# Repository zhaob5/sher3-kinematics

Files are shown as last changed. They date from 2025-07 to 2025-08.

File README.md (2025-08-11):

# SHER-3.0 Kinematics and Jacobian Analysis

This repository contains detailed derivations and explanations of the **forward kinematics**, **inverse kinematics**, **Jacobian**, and **Jacobian Inverse** analysis for the **SHER-3.0 surgical robot**. It includes analytical computation results in Python, validation through SolidWorks motion simulation, and detailed documentation for future insights and reference.

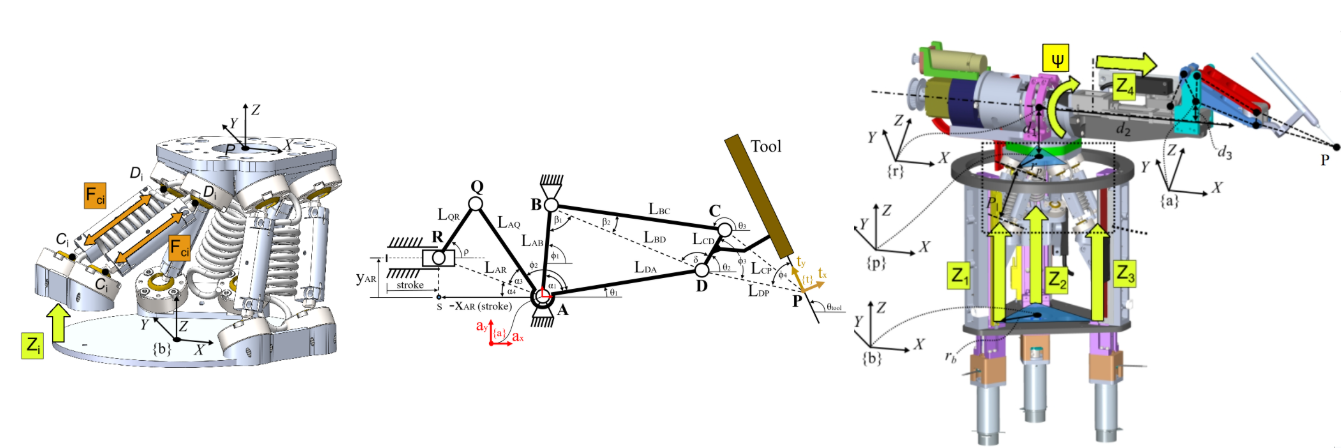
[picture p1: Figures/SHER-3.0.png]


## Recommended reading order:

1. **[Kinematics of a 3-PUU Delta-Style Parallel Robot](https://github.com/zhaob5/sher3-kinematics/blob/main/Kinematics%20of%20a%203-PUU%20Delta-Style%20Parallel%20Robot.pdf)** – foundational understanding of the delta platform.

2. **[Kinematics of the Roll-Tilt Mechanism in SHER-3.0](https://github.com/zhaob5/sher3-kinematics/blob/main/Kinematics%20of%20the%20Roll-Tilt%20Mechanism%20in%20SHER-3.0.pdf)** – breakdown of the rotating four-bar linkage structure.
   
3. **[(Optional) SOLIDWORKS Motion Study Tutorial: Setup and Kinematic Analysis for SHER-3.0](https://github.com/zhaob5/sher3-kinematics/blob/main/SOLIDWORKS%20Motion%20Study%20Tutorial%20Setup%20and%20Kinematic%20Analysis%20for%20SHER-3.0.pdf)** - a quick-start reference for running motion simulation in SOLIDWORKS.

4. **[Kinematics and Jacobian Analysis of SHER-3.0](https://github.com/zhaob5/sher3-kinematics/blob/main/Kinematics%20and%20Jacobian%20Analysis%20of%20SHER-3.0.pdf)** – full system modeling and differential kinematics.

5. **[Closed-Form Jacobian Inverse Derivation for SHER-3.0](https://github.com/zhaob5/sher3-kinematics/blob/main/Closed-Form%20Jacobian%20Inverse%20Derivation%20for%20SHER-3.0.pdf)** - derivation of the Jacobian Inverse with physical intuition.

## License

Copyright © 2025 JHU LCSR. Developed by Botao Zhao for [AMIRo Research Lab](https://amiro.lcsr.jhu.edu/).

See the [LICENSE](./LICENSE) file for details.

## Disclaimer

The derivation and analysis presented in this repository are based on analytical methods applied to a custom-designed robotic system. Readers are strongly encouraged to focus on the **methodology and reasoning** behind the derivations rather than relying solely on the final equations.

**Please independently verify all results before applying them to any critical or safety-sensitive applications.** This work is provided “as is” without warranty of any kind.

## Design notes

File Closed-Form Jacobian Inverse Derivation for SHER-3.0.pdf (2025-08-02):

## Closed-Form Jacobian Inverse Derivation for SHER-3.0

Botao Zhao

August 2, 2025

## Contents

1 Introduction | 2
2 SHER-3.0 at a Glance - and Why It’s Different | 2
3 Spatial Jacobian Inverse | 3
4 Body Jacobian Inverse | 8
5 Jacobian Inverse Validation | 8
6 Disclaimer | 9
7 Appendix: Python Scripts | 10

## 1 Introduction

In my previous work, Kinematics and Jacobian Analysis of SHER-3.0, I demonstrated that the robot’s Jacobian pseudo-inverse can be expressed as J

† = (J
T J)

−1J
T
, which is a common numerical method for computing the inverse. However, while numerical approaches are convenient, having an analytical (closed-form) Jacobian inverse is essential for achieving fast, stable, and insightful control — especially in real-time robotics applications.
For example, a robotic arm running at 500Hz. A numerical Jacobian inverse might take 1.8ms per control cycle - uncomfortably close to the 2ms timing constraint - whereas a symbolic expression, optimized in code, usually could reduce that time to under 0.5ms. Beyond performance, analytical forms also expose singularities, reduce numerical drift, and support optimization routines that rely on clean derivatives. They’re not just elegant - they’re highly practical!
This document walks through the step-by-step derivation of the analytical pseudo-inverse of the Jacobian for SHER-3.0 (Eye Robot 3.0). If you haven’t read my earlier work - especially Kinematics and Jacobian Analysis of SHER-3.0 and related documents, I strongly encourage you to review them first, as this work builds directly on those foundational concepts. Those related documents are avalible at: https://github.com/zhaob5/sher3-kinematics

## 2 SHER-3.0 at a Glance - and Why It’s Different

As mentioned throughout previous work, SHER-3.0 is a hybrid delta-serial robot designed specifi-cally for eye surgery, as illustrated in Fig.(1). Its unique structure, a delta platform coupled with a rotating four-bar linkage, sets it apart from most conventional ophthalmic surgical robots and presents significant challenges to traditional kinematic modeling approaches. My previous work has focused on deriving its kinematics in detail, and I hope those efforts will provide useful insights, or practical guidance for your own work.

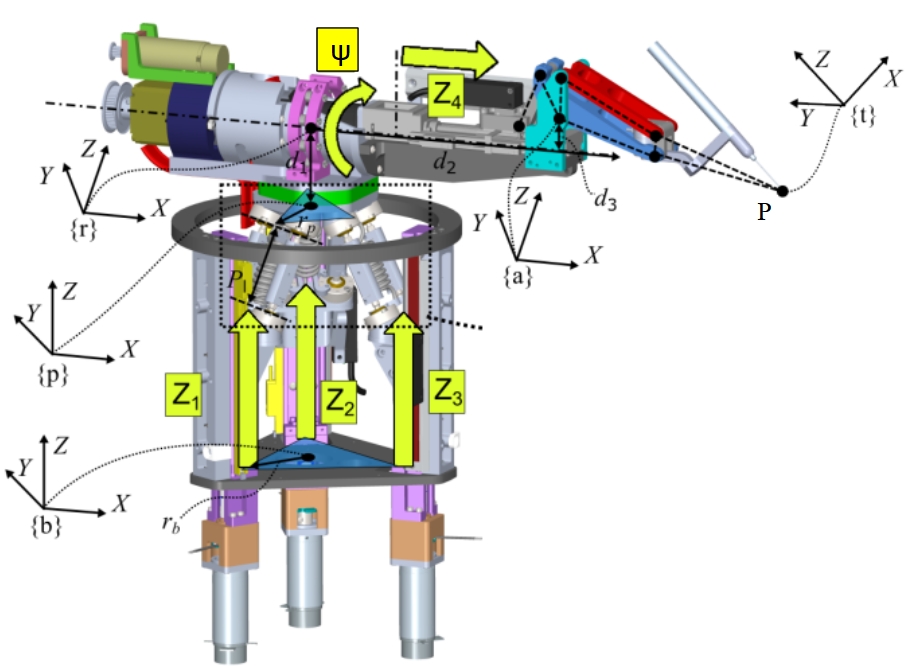
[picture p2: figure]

Figure 1: CAD models of the 5-DOF SHER-3.0 with assigned frames

## 3 Spatial Jacobian Inverse

Since we are not relying on numerical methods to compute the Jacobian inverse, it is important to first revisit its physical meaning. Suppose we want the tool tip to move with a desired spatial velocity Vtool = [ ˙x, y,˙ z,˙

˙θx,

˙θy,

˙θz]
T
. To achieve this motion, the robot must drive its joints at specific velocities ˙q = [ ˙q1, q˙2, q˙3, q˙4, q˙5]

T
. But how do we determine the required joint motions? This is where the Jacobian inverse comes in: it provides the mapping from task-space velocity to joint-space velocity. Our goal, therefore, is to derive this mapping from first principles, guided by physical intuition rather than black-box computation.

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
For simplicity, all Jacobians discussed in this section refer to the spatial Jacobian, and velocities are expressed in base frame.

Recall from Section-5.2 of Kinematics of a 3-PUU Delta-Style Parallel Robot, we derived the differential kinematics of the delta platform:

zli

q˙i = xlix˙ + yli

y˙ + zli

z˙ | (2)

where i = 1, 2, 3, and xli

, yli

, zli

are the x, y, z components of the vector along link li | . Here, ˙qi
denotes the linear velocity of the i-th prismatic joint, and ˙x, y,˙ z˙ represent the translational velocity of the delta platform in the base frame.

From this, we can directly relate the desired platform velocity to the corresponding joint velocities as:

q˙i =

xli
zli

x˙ +

yli
zli
y˙ + ˙z | (3)

Now, focusing just on the delta platform - if we know the desired linear velocity of the platform, the corresponding joint velocities can be directly computed from it as:

q˙1
q˙2
q˙3

delta

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
- (4)

This relationship effectively defines the top-left block of the Jacobian inverse.

Now let’s do some visualization: Although the roll and tilt joints appear to provide only angular motion, the tool tip is not located along their axes of rotation (as illustrated in Fig.2). In fact, due to the four-bar linkage, the tilt motion is mechanically coupled with translation. As a result, both roll and tilt inevitably produce linear motion in the x, y, z directions.

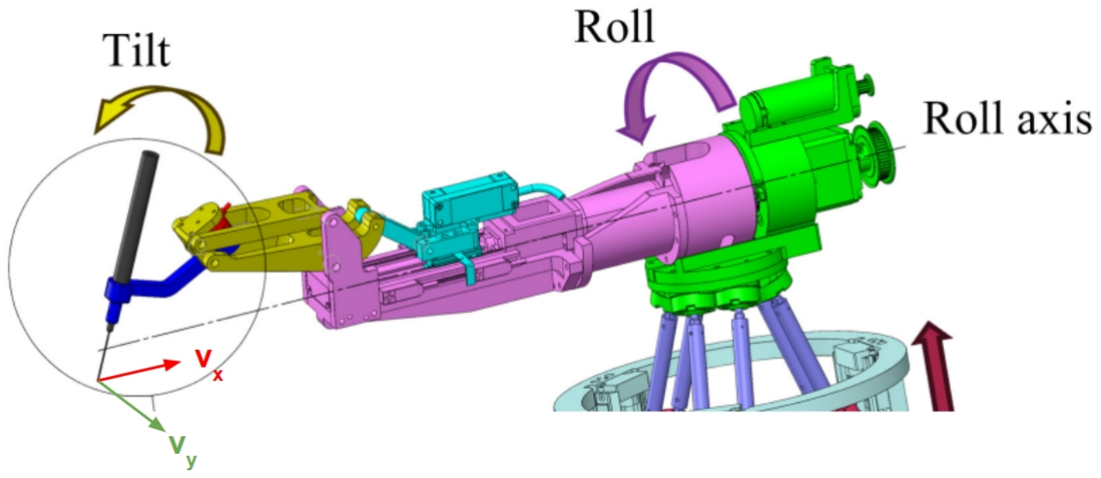
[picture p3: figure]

Figure 2: Roll-Tilt Mechanism and Induced Velocities vx and vy

Here comes the most challenging part to imagine: although angular velocities ˙θx,

˙θy,

˙θz will cause
nonzero ˙x, y,˙ z˙, these induced translations can be computed precisely. So, to isolate the translation purely caused by the roll-tilt mechanism, we can simply compensate (by subtracting) these induced linear velocities with the delta platform.

How do we know the linear velocity of tool tip in frame {p}? If we just look the roll-tilt mechanism, as we derived previously in Kinematics of the Roll-Tilt Mechanism in SHER-3.0, the translational velocity induced by the roll-tilt mechanism can be expressed as:

x˙
y˙
z˙

{p}

=

P˙
x{a}
− sin(ψ)P˙

y{a} − cos(ψ)ψ˙(Py{a} + d3) cos(ψ)P˙

y{a} − sin(ψ)ψ˙(Py{a} + d3)

- (5)

where

P˙

x{a} = − sin(θ1)LDA ˙θ1 − sin(θ2 − ϕ3)LDP ˙θ2

P˙

y{a} = cos(θ1)LDA ˙θ1 + cos(θ2 − ϕ3)LDP ˙θ2

(6)

and previously, we also derived the angular velocity of each link:

˙θ1 = −

LID

LDA

˙θ2

˙θ2 =

LDALJQ

LIDLAQLJR

s˙

(7)

Plug eq.(7) into eq.(6):

P˙
x{a} = (sin(θ1)LID − sin(θ2 − ϕ3)LDP )

˙θ2

P˙
y{a} = (− cos(θ1)LID + cos(θ2 − ϕ3)LDP )

˙θ2

(8)

Let:

C = sin(θ1)LID − sin(θ2 − ϕ3)LDP D = − cos(θ1)LID + cos(θ2 − ϕ3)LDP

(9)

Then

P˙

x{a} = C ˙θ2

P˙

y{a} = D ˙θ2

(10)

By plugging eq.(5) into eq.(4), we obtain the joint velocities required to compensate for the induced linear motion:

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
x{a}
− sin(ψ)P˙

y{a} − cos(ψ)ψ˙(Py{a} + d3) cos(ψ)P˙

y{a} − sin(ψ)ψ˙(Py{a} + d3)

(11)

Since we’re interested in understanding how the roll and tilt mechanisms contribute to this induced velocity, we aim to express eq.(11) explicitly in terms of the roll and tilt rates ψ˙ and ˙θ2. Substituting eq.(10) into eq.(11) yields:

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
C ˙θ2
− sin(ψ)D ˙θ2 − cos(ψ)(Py{a} + d3)ψ˙ cos(ψ)D ˙θ2 − sin(ψ)(Py{a} + d3)ψ˙

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
0 | C
− cos(ψ)(Py{a} + d3) − sin(ψ)D − sin(ψ)(Py{a} + d3) cos(ψ)D

ψ˙
˙θ2

=

−

yl1

zl1

cos(ψ)(Py{a} + d3) − sin(ψ)(Py{a} + d3)

xl1

zl1

C −

yl1

zl1

sin(ψ)D + cos(ψ)D
−

yl2

zl2

cos(ψ)(Py{a} + d3) − sin(ψ)(Py{a} + d3)

xl2

zl2

C −

yl2

zl2

sin(ψ)D + cos(ψ)D
−

yl3

zl3

cos(ψ)(Py{a} + d3) − sin(ψ)(Py{a} + d3)

xl3

zl3

C −

yl3

zl3

sin(ψ)D + cos(ψ)D

ψ˙
˙θ2

(12)

Now we have established the relationship between the joint velocities required to compensate for the induced linear motion and the angular velocities of the roll and tilt mechanisms.

However, we want to express these angular velocities in the base frame as [ ˙θx,

˙θy,

˙θz]
T
. To do
so, let’s recall the expression for the tool tip’s angular velocity previously derived in Kinematics of the Roll-Tilt Mechanism in SHER-3.0 :

˙θx
˙θy
˙θz

{p}

=

ψ˙
− cos(ψ)

˙θ2
− sin(ψ)

˙θ2

- (13)

Since there’s no rotational transformation between base frame {b} and delta platform frame {p}, it’s easy to figure out [ ˙θx,

˙θy,

˙θz]
T

{p} = [ ˙θx,

˙θy,

˙θz]
T
{b}

From eq.(13), it’s clear that although ˙θy and ˙θz appear to be independent, they are actually coupled through ψ and ˙θ2. In other words, specifying ˙θy determines a unique corresponding ˙θz and vice versa.
Since ψ˙ represents the rotational velocity about the base frame’s x axis, and we already have the relationship between ˙θy and ˙θ2 from eq.(13), we can substitute ψ˙ = ˙θx and ˙θ2 = −
1
cos(ψ)

˙θy into

eq.(12) to obtain:

q˙1
q˙2
q˙3
- =

−

yl1

zl1

cos(ψ)(Py{a} + d3) − sin(ψ)(Py{a} + d3)

xl1

zl1

C −

yl1

zl1

sin(ψ)D + cos(ψ)D
−

yl2

zl2

cos(ψ)(Py{a} + d3) − sin(ψ)(Py{a} + d3)

xl2

zl2

C −

yl2

zl2

sin(ψ)D + cos(ψ)D
−

yl3

zl3

cos(ψ)(Py{a} + d3) − sin(ψ)(Py{a} + d3)

xl3

zl3

C −

yl3

zl3

sin(ψ)D + cos(ψ)D

"
˙θx
−

1
cos(ψ)

˙θy

=

−

yl1

zl1

cos(ψ)(Py{a} + d3) − sin(ψ)(Py{a} + d3) −

xl1

zl1

cos(ψ)

C +

yl1

zl1

tan(ψ)D − D
−

yl2

zl2

cos(ψ)(Py{a} + d3) − sin(ψ)(Py{a} + d3) −

xl2

zl2

cos(ψ)

C +

yl2

zl2

tan(ψ)D − D
−

yl3

zl3

cos(ψ)(Py{a} + d3) − sin(ψ)(Py{a} + d3) −

xl3

zl3

cos(ψ)

C +

yl3

zl3

tan(ψ)D − D

˙θx
˙θy

(14)

Let

Mr =

−

yl1

zl1

cos(ψ)(Py{a} + d3) − sin(ψ)(Py{a} + d3) −

xl1

zl1

cos(ψ)

C +

yl1

zl1

tan(ψ)D − D
−

yl2

zl2

cos(ψ)(Py{a} + d3) − sin(ψ)(Py{a} + d3) −

xl2

zl2

cos(ψ)

C +

yl2

zl2

tan(ψ)D − D
−

yl3

zl3

cos(ψ)(Py{a} + d3) − sin(ψ)(Py{a} + d3) −

xl3

zl3

cos(ψ)

C +

yl3

zl3

tan(ψ)D − D

(15)

Then

q˙1
q˙2
q˙3

induced

= Mr

˙θx
˙θy

{b}

(16)

In this case, it’s clear that ˙θz has no effect on ˙q1, q˙2, q˙3. However, to maintain consistency with the full Jacobian inverse expression introduced later, we’ll add ˙θz to the right-hand side of eq.(16) to make it consistancy with later Jacobian Inverse expression:

q˙1
q˙2
q˙3

induced

= [Mr 0]

˙θx
˙θy
˙θz

{b}

(17)

Now, let’s combine eq.(4) and eq.(17). Note that the joint velocities from eq.(17) represent the linear velocity induced by roll and tilt, which is exactly the term that needs to be subtracted in our final Jacobian inverse formulation.

Thus:

q˙1
q˙2
q˙3
- =

q˙1
q˙2
q˙3

delta

−

q˙1
q˙2
q˙3

induced

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
- − [Mr 0]

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
1 −Mr[1,1] | −Mr[1,2] | 0

xl2

zl2

yl2

zl2

1 −Mr[2,1] | −Mr[2,2] | 0

xl3

zl3

yl3

zl3

1 −Mr[3,1] | −Mr[3,2] | 0

x˙
y˙
z˙
˙θx
˙θy
˙θz

{b}

(18)

From eq.(7), since ˙s = ˙q5 and ˙θ2 = −
1
cos(ψ)

˙θy, we can get the relationship between ˙q5 and ˙θy:

˙θ2 =

LDALJQ

LIDLAQLJR

s˙

−

1
cos(ψ)

˙θy =

LDALJQ

LIDLAQLJR

q˙5

(19)

Recall ψ is just q4. Rearrange eq.(19), and we will get:

q˙5 = −

LIDLAQLJR
cos(q4)LDALJQ
˙θy | (20)

Since ˙q4 = ψ˙ represents the rotational velocity about the base frame’s x axis,

q˙4 = ˙θx | (21)

Thus, we now have the final two components needed to construct the Jacobian inverse. By stacking eq.(20) and eq.(21) to eq.(18), we obtain:

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
1 −Mr[1,1] | −Mr[1,2] | 0

xl2

zl2

yl2

zl2

1 −Mr[2,1] | −Mr[2,2] | 0

xl3

zl3

yl3

zl3

1 −Mr[3,1] | −Mr[3,2] | 0
0 | 0 | 0 | 1 | 0 | 0
0 | 0 | 0 | 0 | −
| | | | LIDLAQLJR cos(q4)LDALJQ | 0

x˙
y˙
z˙
˙θx
˙θy
˙θz

(22)

Finally, the analytical expression of Spatial Jacobian Inverse is:

Js

−1 =

xl1

zl1

yl1

zl1

1 −Mr[1,1] | −Mr[1,2] | 0

xl2

zl2

yl2

zl2

1 −Mr[2,1] | −Mr[2,2] | 0

xl3

zl3

yl3

zl3

1 −Mr[3,1] | −Mr[3,2] | 0
0 | 0 | 0 | 1 | 0 | 0
0 | 0 | 0 | 0 | −
| | | | LIDLAQLJR cos(q4)LDALJQ | 0

(23)

## 4 Body Jacobian Inverse

In Kinematics and Jacobian Analysis of SHER-3.0, we defined a simplified adjoint-like mapping Ad†
(Tbt)

using only the rotation matrix:

Ad†
(Tbt) =
Rbt | 0
0 | Rbt
(24)

where Tbt is the homogeneous transformation from base frame {b} to tool frame {t}, and rotation matrix Rbt = Tbt[: 3, : 3].

Recall the relationship between Spatial and Body Jacobians:

Jb = Ad†
(Tbt)

−1
Js | (25)

Thus, we get the expression of the Body Jacobian Inverse:

Jb

−1 = Js

−1Ad†
(Tbt)

(26)

## 5 Jacobian Inverse Validation

In Kinematics and Jacobian Analysis of SHER-3.0, we previously verified the correctness of the forward Jacobian. Therefore, we will use that validated Jacobian as the ground truth Jtrue(q) in this section to verify the analytical Jacobian Inverse. The Python script used for verification is provided in the appendix.

To perform the verification, we first assign arbitrary joint positions q and joint velocities ˙qd. Using the verified Jacobian, we compute the corresponding tool tip velocities. These velocities are then fed into the Jacobian Inverse model. If the output joint velocities match the originally assigned (desired) values, the Jacobian Inverse is considered correct.

The verification workflow is as follows:

Vtool = Jtrue(q)˙qd

˙q = J(q)

−1Vtool

(27)

If ˙q = ˙qd, then the Jacobian Inverse is correct.

Consider the following random joint positions and velocities

q1
q2
q3
q4
q5

=

1 mm
2 mm
3 mm
31π
180 rad
11 mm

,

q˙1
q˙2
q˙3
q˙4
q˙5

=

7 mm/s
8 mm/s
9 mm/s
10π
180 rad/s
15 mm/s

The results are shown below:

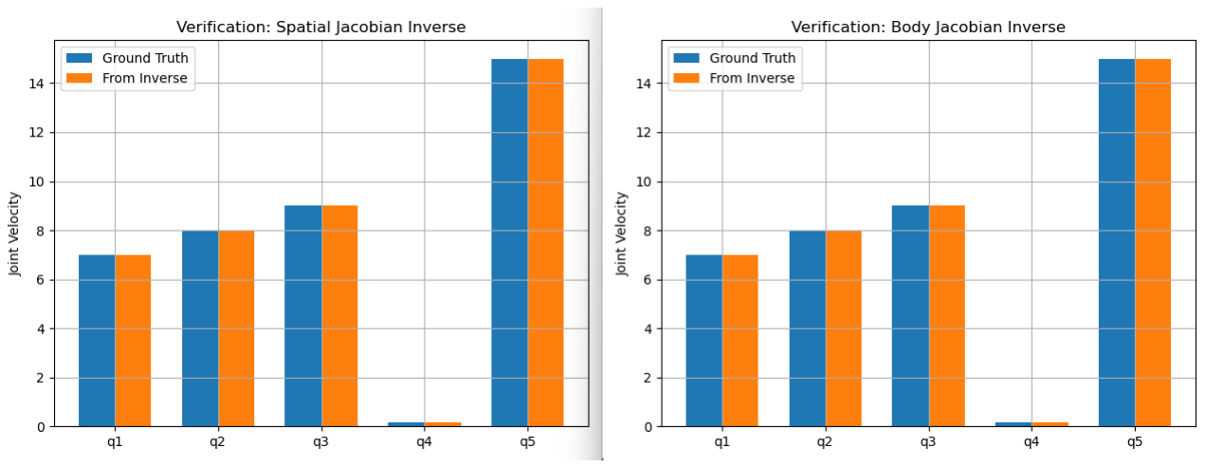
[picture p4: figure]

Figure 3: Joint Velocities Comparison

The joint velocities reconstructed using the analytical Jacobian inverse match the ground truth values across all joints. Thus, it confirms that the transformation from task-space velocities to joint-space velocities is accurate under the current kinematic model.

## 6 Disclaimer

The derivation process for the closed-form Jacobian inverse presented in this document is extremely tedious and prone to algebraic complexity. While every effort has been made to ensure the accuracy of the results, readers are strongly encouraged to focus on understanding the methodology and reasoning behind each step rather than relying solely on the final equations. If you plan to use these results in any critical applications, please independently verify all expressions and calculations for your specific use case. If you spot any errors, have suggestions, or would like to discuss the topic further, feel free to reach out to me at: bzhao17@alumni.jh.edu.

## 7 Appendix: Python Scripts

### 7.1 Jacobian Inverse Validation

1 | # -*- coding: utf-8 -*-
2 | """
3 | Created on Wed Jul 30 13:17:00 2025

4
5 | @author: Botao Zhao
6 | """

7
8 | import numpy as np
9 | from sympy import Matrix, zeros, pprint
10 | import matplotlib.pyplot as plt

11
12 | ################### Adjoint-like Mapping ###########################
13 | def adjoint_pseudo(T):
14 | R = T[:3, :3]
15 | return Matrix.vstack(
16 | Matrix.hstack(R, Matrix.zeros(3)),
17 | Matrix.hstack(Matrix.zeros(3), R)
18 | )

19
20 | ################### Joint Parameters: ##############################
21 | # Set desired Joint Positions Here:
22 | q1 = 1 | # Prismatic
23 | q2 = 2 | # Prismatic
24 | q3 = 3 | # Prismatic
25 | q4 = 31*np.pi/180 | # Revolute
26 | q5 = 11 | # Prismatic

27
28 | ################### Joint Velocities: ##############################
29 | # Set desired Joint Velocities Here:
30 | q1_dot = 7 | # mm/s
31 | q2_dot = 8 | # mm/s
32 | q3_dot = 9 | # mm/s
33 | q4_dot = 10*np.pi/180 | # rad/s
34 | q5_dot = 15 | # mm/s
35 | q_dot = Matrix([
36 | [q1_dot],
37 | [q2_dot],
38 | [q3_dot],
39 | [q4_dot],
40 | [q5_dot]
41 | ])

42
43 | ############################ Delta Platform: ###############################
44 | # Robot parameters
45 | rp = 34.4773 # mm platform radius
46 | rb = 60.6927 # mm base radius
47 | l = 68 | # mm rod length

48
49 | # Base joint angles
50 | theta1 = np.pi / 3
51 | theta2 = np.pi
52 | theta3 = 5 * np.pi / 3

53
54 | # Base joint positions (fixed)
55 | rb1 = np.array([np.cos(theta1)*rb, np.sin(theta1)*rb, 0])

rb2 = np.array([np.cos(theta2)*rb, np.sin(theta2)*rb, 0]) rb3 = np.array([np.cos(theta3)*rb, np.sin(theta3)*rb, 0])

# Platform offsets (relative to center)

rp1 = np.array([np.cos(theta1)*rp, np.sin(theta1)*rp, 0]) rp2 = np.array([np.cos(theta2)*rp, np.sin(theta2)*rp, 0]) rp3 = np.array([np.cos(theta3)*rp, np.sin(theta3)*rp, 0])

L1 = np.array([0,0,q1])
L2 = np.array([0,0,q2])
L3 = np.array([0,0,q3])

e1 = L1 + rb1 - rp1
e2 = L2 + rb2 - rp2
e3 = L3 + rb3 - rp3

h1 = ((e2[0]**2 + e2[1]**2 + e2[2]**2) - (e1[0]**2 + e1[1]**2 + e1[2]**2))/2 h2 = ((e3[0]**2 + e3[1]**2 + e3[2]**2) - (e1[0]**2 + e1[1]**2 + e1[2]**2))/2

x21 = (e2 - e1)[0]
y21 = (e2 - e1)[1]
z21 = (e2 - e1)[2]

x31 = (e3 - e1)[0]
y31 = (e3 - e1)[1]
z31 = (e3 - e1)[2]

k1 = (y31*z21/y21 - z31)/(x31 - y31*x21/y21) k2 = (h2 - y31*h1/y21)/(x31 - y31*x21/y21) k3 = (x31*z21/x21 - z31)/(y31 - x31*y21/x21) k4 = (h2 - x31*h1/x21)/(y31 - x31*y21/x21)

T1 = k1**2 + k3**2 + 1
T2 = k1*k2 + k3*k4 - e1[0]*k1 - e1[1]*k3 - e1[2]
T3 = k2**2 + k4**2 -2*e1[0]*k2 - 2*e1[1]*k4 - l**2 + e1[0]**2 + e1[1]**2 + e1[2]**2

z = (-T2 + np.sqrt(T2**2 - T1*T3))/T1
x = k1*z + k2
y = k3*z + k4

r = np.array([x, y, z])

l1 = -L1 - rb1 + r + rp1
l2 = -L2 - rb2 + r + rp2
l3 = -L3 - rb3 + r + rp3

########################## Roll-Tilt Mechanism: ###########################

s = q5 # slider linear actuator
s_dot = q5_dot # slider velocity
psi = q4 # roll angle

# Fixed Parameters

x_AR_max = 60.48
y_AR = -10
L_AQ = 32.5
L_QR = 42

L_AB = 28
L_BC = 78.5
L_CD = 15
L_DA = 73.5
phi1 = np.pi / 2
phi2 = np.pi * 138 / 180
L_DP = 94.49
phi3 = np.pi * 103.93 / 180
phi4 = np.pi * 31.06 / 180
L_T = 50
d1 = 56.01 # Distance between the center frame of the delta platform to point A d2 = 192.7
d3 = 25.5

# Fixed angles in radians

phi1 = np.pi / 2
phi2 = np.pi * 138 / 180
phi3 = np.pi * 103.93 / 180 phi4 = np.pi * 31.06 / 180

# Position Analysis

x_AR = x_AR_max - s
L_AR = np.sqrt(x_AR**2 + y_AR**2)
alpha3 = np.arccos((L_AR**2 + L_AQ**2 - L_QR**2) / (2 * L_AR * L_AQ)) alpha4 = np.pi - np.arctan2(y_AR, -x_AR)
alpha = alpha3 + alpha4

theta1 = np.pi - (phi2 + alpha3 + alpha4)
alpha_1 = phi1 - theta1
L_BD = np.sqrt(L_AB**2 + L_DA**2 - 2 * L_AB * L_DA * np.cos(alpha_1)) beta_1 = np.arccos((L_AB**2 + L_BD**2 - L_DA**2) / (2 * L_AB * L_BD))

delta = np.arccos((L_CD**2 + L_BD**2 - L_BC**2) / (2 * L_CD * L_BD)) theta2 = phi1 + beta_1 - delta

# Velocity Analysis

L_JR = np.tan(alpha)*x_AR - y_AR
L_JQ = np.sqrt((L_JR+y_AR)**2 + x_AR**2) - L_AQ

rho_dot = s_dot / L_JR
theta1_dot = -L_JQ / L_AQ * rho_dot

beta_2 = np.arccos((L_BC**2 + L_BD**2 - L_CD**2) / (2 * L_BC * L_BD)) L_IA = L_AB * np.sin(beta_1 + beta_2) / np.sin(alpha_1 + beta_1 + beta_2) L_ID = L_IA - L_DA

theta2_dot = -L_DA / L_ID * theta1_dot

# Position in {a} frame:

px_a = np.cos(theta1)*L_DA + np.cos(theta2 - phi3)*L_DP py_a = np.sin(theta1)*L_DA + np.sin(theta2 - phi3)*L_DP

# Position in {p} frame:

px_p = px_a + d2
py_p = -np.sin(psi)*py_a - np.sin(psi)*d3 pz_p = np.cos(psi)*py_a + np.cos(psi)*d3 + d1

# Position in {b} frame:

px_b = px_a + d2 + x py_b = -np.sin(psi)*py_a - np.sin(psi)*d3 + y pz_b = np.cos(psi)*py_a + np.cos(psi)*d3 + d1 + z

# print([px_p, py_p, pz_p])

########## Homogeneous Transformation from Base frame to Tool frame ########### # Tbt

theta = np.pi/2 - phi4 - phi3 + theta2
Tbt = Matrix([
[np.cos(theta), -np.sin(theta), 0, px_a+d2+x],
[-np.sin(theta)*np.sin(psi), -np.cos(theta)*np.sin(psi), -np.cos(psi), -np.sin(psi)*py_a-np.sin(psi)*d3+y], [np.sin(theta)*np.cos(psi), np.cos(theta)*np.cos(psi), -np.sin(psi), np.cos(psi)*py_a+np.cos(psi)*d3+d1+z], [0, 0, 0, 1]
]) # 4x4 transformation from base to tool
Rbt = Tbt[:3, :3]

# Compute Ad_Tbt¹

Ttb = Tbt.inv()
Ad_Ttb = adjoint_pseudo(Ttb)

################### Spatial Jacobian Inverse (Analytical) #################

JacobianInvTip = zeros(5,6)

C = np.sin(theta1)*L_ID - np.sin(theta2-phi3)*L_DP D = -np.cos(theta1)*L_ID + np.cos(theta2-phi3)*L_DP

M_r = zeros(3,2)
M_r[0,0] = -l1[1]/l1[2] * np.cos(psi) * (py_a + d3) - np.sin(psi)*(py_a + d3) M_r[0,1] = -l1[0]/(l1[2]*np.cos(psi)) * C + l1[1]/l1[2]*np.tan(psi)*D - D

M_r[1,0] = -l2[1]/l2[2] * np.cos(psi) * (py_a + d3) - np.sin(psi)*(py_a + d3) M_r[1,1] = -l2[0]/(l2[2]*np.cos(psi)) * C + l2[1]/l2[2]*np.tan(psi)*D - D

M_r[2,0] = -l3[1]/l3[2] * np.cos(psi) * (py_a + d3) - np.sin(psi)*(py_a + d3) M_r[2,1] = -l3[0]/(l3[2]*np.cos(psi)) * C + l3[1]/l3[2]*np.tan(psi)*D - D

JacobianInvTip[0,0] = l1[0]/l1[2]
JacobianInvTip[1,0] = l2[0]/l2[2]
JacobianInvTip[2,0] = l3[0]/l3[2]

JacobianInvTip[0,1] = l1[1]/l1[2] JacobianInvTip[1,1] = l2[1]/l2[2] JacobianInvTip[2,1] = l3[1]/l3[2]

JacobianInvTip[0,2] = 1
JacobianInvTip[1,2] = 1
JacobianInvTip[2,2] = 1

JacobianInvTip[0:3, 3:5] = -M_r

JacobianInvTip[3,3] = 1

JacobianInvTip[4,4] = -L_ID*L_AQ*L_JR/(np.cos(q4)*L_DA*L_JQ)

JacobianInvTip[4,5] = 0 #

233
234 Js_inv = JacobianInvTip # 5x6 Spatial Jacobian Inverse

235

236

237
238 | ################ Body Jacobian Inverse | (Analytical) ################
239 | Ad_Tbt = adjoint_pseudo(Ttb).T

240
241 | # Compute body Jacobian
242 | Jb_inv = Js_inv * Ad_Tbt # 5x6 Body Jacobian Inverse

243

244
245 | ################ Spatial Jacobian ##############
246 | J_l = zeros(3,3)

247
248 | J_l[0,0] = l1[0]
249 | J_l[0,1] = l1[1]
250 | J_l[0,2] = l1[2]
251 | J_l[1,0] = l2[0]
252 | J_l[1,1] = l2[1]
253 | J_l[1,2] = l2[2]
254 | J_l[2,0] = l3[0]
255 | J_l[2,1] = l3[1]
256 | J_l[2,2] = l3[2]

257
258 J_z = zeros(3,3)

259
260 | J_z[0,0] = l1[2]
261 | J_z[1,1] = l2[2]
262 | J_z[2,2] = l3[2]

263
264 J_d = J_l.inv() * J_z

265
266 | A = np.sin(theta1)*L_DA*L_JQ/(L_AQ*L_JR) - np.sin(theta2-phi3)*L_DP*L_DA*L_JQ/(L_ID*L_AQ*L_JR)
267 | B = -np.cos(theta1)*L_DA*L_JQ/(L_AQ*L_JR) + np.cos(theta2-phi3)*L_DP*L_DA*L_JQ/(L_ID*L_AQ*L_JR)

268
269 JacobianTip = zeros(6,5)

270
271 JacobianTip[:3, :3] = J_d

272
273 | JacobianTip[1,3] = -np.cos(q4)*(py_a + d3)
274 | JacobianTip[2,3] = -np.sin(q4)*(py_a + d3)
275 | JacobianTip[3,3] = 1

276
277 | JacobianTip[0,4] = A
278 | JacobianTip[1,4] = -np.sin(q4)*B
279 | JacobianTip[2,4] = np.cos(q4)*B
280 | JacobianTip[4,4] = -np.cos(q4)*L_DA*L_JQ/(L_ID*L_AQ*L_JR)
281 | JacobianTip[5,4] = -np.sin(q4)*L_DA*L_JQ/(L_ID*L_AQ*L_JR)

282
283 | Js = JacobianTip | # 6x5 spatial Jacobian

284

285

286
287 ################# Body Jacobian ###################

288
289 # Tbt is known

290
291 # Compute body Jacobian

Jb = Ad_Ttb * Js

################# Tool Tip Velocity ################## V_tool_t = Jb*q_dot

V_tool_b = Js*q_dot

# print("\nIn base frame:\n")

# print("x_dot_b = ", V_tool_b[0], "mm/s")

# print("y_dot_b = ", V_tool_b[1], "mm/s")

# print("z_dot_b = ", V_tool_b[2], "mm/s")

# print("theta_x_dot_b = ", V_tool_b[3]*180/np.pi, "deg/s") # print("theta_y_dot_b = ", V_tool_b[4]*180/np.pi, "deg/s") # print("theta_z_dot_b = ", V_tool_b[5]*180/np.pi, "deg/s\n")

# print("\nIn tool frame:\n")

# print("x_dot_t = ", V_tool_t[0], "mm/s")

# print("y_dot_t = ", V_tool_t[1], "mm/s")

# print("z_dot_t = ", V_tool_t[2], "mm/s")

# print("theta_x_dot_t = ", V_tool_t[3]*180/np.pi, "deg/s") # print("theta_y_dot_t = ", V_tool_t[4]*180/np.pi, "deg/s") # print("theta_z_dot_t = ", V_tool_t[5]*180/np.pi, "deg/s\n")

################ Jacobian Inverse Verification ##################

q_dot_verify_s = Js_inv * V_tool_b
q_dot_verify_b = Jb_inv * V_tool_t

# print("Joint Velocity from Jacobian Pseudo-Inverse:")

# print("q_dot_s =")

# pprint(q_dot_verify_s) # The results should match your q_dot values # print("q_dot_b =")

# pprint(q_dot_verify_b) # The results should match your q_dot values

################### Visualization ##############################

def visualize_joint_velocity_comparison(original, computed, title): original_np = np.array(original).astype(np.float64).flatten() computed_np = np.array(computed).astype(np.float64).flatten()

joint_labels = [f'q{i+1}' for i in range(len(original_np))] x = np.arange(len(joint_labels))
width = 0.35

fig, ax = plt.subplots()
ax.bar(x - width/2, original_np, width, label='Ground Truth') ax.bar(x + width/2, computed_np, width, label='From Inverse')

ax.set_ylabel('Joint Velocity')
ax.set_title(title)
ax.set_xticks(x)
ax.set_xticklabels(joint_labels) ax.legend()
ax.grid(True)

plt.tight_layout()

351 | plt.show()

352
353 | # Visualize results
354 | visualize_joint_velocity_comparison(q_dot, q_dot_verify_s, "Verification: Spatial Jacobian Inverse")
355 | visualize_joint_velocity_comparison(q_dot, q_dot_verify_b, "Verification: Body Jacobian Inverse")

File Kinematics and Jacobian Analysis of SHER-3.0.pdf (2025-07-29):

## Kinematics and Jacobian Analysis of SHER-3.0

Botao Zhao

July 29, 2025

## Contents

1 Introduction | 2
2 System Overview | 2
3 Jacobian Matrix of SHER-3.0 | 3
4 Jacobian Pseudo-inverse of SHER-3.0 | 7
5 Validation with SolidWorks Motion Analysis | 8
6 Disclaimer | 11
7 Appendix: Python Scripts | 12

## 1 Introduction

The purpose of this document is to show detailed derivation of Jacobian matrix and Jacobian pseudo-inverse of SHER-3.0 (Eye Robot 3.0). Two separate documents covering the kinematic derivation of the delta platform and the roll-tilt mechanism are available at https://github.com/zhaob5/delta_kinematics (https://github.com/zhaob5/delta_kinematics) and https://github.com/zhaob5/roll_tilt_mechanism. If you haven’t read them yet, I strongly encourage you to review those two documents, as a lot expla-nations here build upon concepts introduced there. Some related papers and scripts can be found on this github page: https://github.com/zhaob5/Kinematics-and-Jacobian-Analysis-of-SHER-3. 0 (https://github.com/zhaob5/Kinematics-and-Jacobian-Analysis-of-SHER-3.0)

## 2 System Overview

The base of SHER-3.0 is a delta mechanism, which has been described in detail in my previous work. Mounted on top of the delta stage is an arm with roll and tilt functionality. The tilt mechanism was designed with a four-bar linkage configuration, as illustrated in Fig.(1) and Fig.(2).


Figure 1: CAD models of the 5-DOF SHER-3.0 with assigned frames

## 3 Jacobian Matrix of SHER-3.0

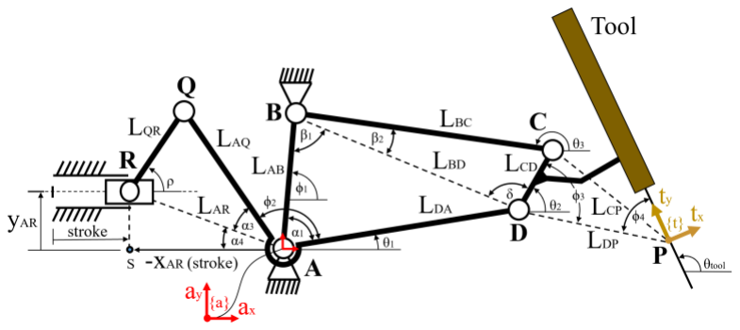
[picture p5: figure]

Figure 2: Side view of the tilt mechanism

### 3.1 Homogeneous Transformation from Base Frame to Tool Frame

Note that the coordinate frames {a} and {t} shown in Fig.1 and Fig.2 have different orientations. In this document, I will use the frame definition shown in Fig.2 to maintain consistency with my previous documentation. If a different frame is chosen, the resulting expressions will differ accordingly.

Since the delta platform provides only translational motion along x, y, z, its homogeneous transformation matrix has the following form:

Tbp =

I r
0 1
(1)

where r = [rx, ry, rz]

T
is the position vector from base frame {b} to platform frame {p}.

In Kinematics of the Roll-Tilt Mechanism in SHER-3.0, we derived:

Tat =

cos(θ) − sin(θ) 0 Px
sin(θ) | cos(θ) | 0 Py
0 | 0 | 1 | 0
0 | 0 | 0 | 1

(2)

Tpa =

1 | 0 | 0 | d2
0 − sin(ψ) − cos(ψ) | − sin(ψ)d3
0 | cos(ψ) | − sin(ψ) cos(ψ)d3 + d1
0 | 0 | 0 | 1

(3)

Thus, the transformation from base frame to tool frame is:

Tbt = TbpTpaTat

=

cos(θ) | − sin(θ) | 0 | Px + d2 + rx
− sin(θ) sin(ψ) − cos(θ) sin(ψ) − cos(ψ) | − sin(ψ)Py − sin(ψ)d3 + ry
sin(θ) cos(ψ) | cos(θ) cos(ψ) | − sin(ψ) cos(ψ)Py + cos(ψ)d3 + d1 + rz
0 | 0 | 0 | 1

(4)

### 3.2 Spatial Jacobian

A brief recap of the Spatial Jacobian: it maps joint velocities to the tool tip velocity, vtool = [ ˙x, y,˙ z,˙

˙θx,

˙θy,

˙θz]
T
, expressed in the base frame {b}.

x˙
y˙
z˙
˙θx
˙θy
˙θz

{b}

= Js

q˙1
q˙2
q˙3
q˙4
q˙5

(5)

Since q1, q2, q3 only generate translational motion, the upper-left 3×3 block of the Spatial Jacobian Js corresponds to the Jacobian of the delta platform, Jd, which was derived in Kinematics of a 3-PUU Delta-Style Parallel Robot:

Jd =

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
| 0 | 0
0 | zl2 | 0
0 | 0 | zl3
- (6)

Similarly, the lower-right 3×2 block of the Spatial Jacobian is only related to q4 and q5 since only q4 and q5 can provide rotational velocity.

Now things become a bit more complex. As previously mentioned, due to the nature of the four-bar linkage, q5 induces both rotational and translational motion, and q4 contributes to linear velocity as well, since the tool tip is offset from its axis of rotation.

Let’s break this down and construct the Spatial Jacobian one by one.

Recall in Kinematics of the Roll-Tilt Mechanism in SHER-3.0, we derived the tool tip velocity in the delta platform frame {p} as:

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
x{a}
− sin(ψ)P˙

y{a} − cos(ψ)ψ˙(Py{a} + d3) cos(ψ)P˙

y{a} − sin(ψ)ψ˙(Py{a} + d3) ψ˙
− cos(ψ)

˙θ2
− sin(ψ)

˙θ2

(7)

where
P˙

x{a} = − sin(θ1)LDA ˙θ1 − sin(θ2 − ϕ3)LDP ˙θ2

P˙

y{a} = cos(θ1)LDA ˙θ1 + cos(θ2 − ϕ3)LDP ˙θ2

θ1 = 180◦ − (ϕ2 + α3 + α4)

θ2 = β1 + ϕ1 − δ

(8)

and previously, we also derived the angular velocity of each link:

˙θ1 = −

LID

LDA

˙θ2

˙θ2 =

LDALJQ

LIDLAQLJR

s˙

(9)

Plug eq.(9) into eq.(8):

P˙
x{a} =
sin(θ1)

LDALJQ

LAQLJR

− sin(θ2 − ϕ3)

LDPLDALJQ

LIDLAQLJR
s˙

P˙
y{a} =
− cos(θ1)

LDALJQ

LAQLJR

+ cos(θ2 − ϕ3)

LDPLDALJQ

LIDLAQLJR
s˙

(10)

Let:

A =

sin(θ1)

LDALJQ

LAQLJR

− sin(θ2 − ϕ3)

LDPLDALJQ

LIDLAQLJR

B =

− cos(θ1)

LDALJQ

LAQLJR

+ cos(θ2 − ϕ3)

LDPLDALJQ

LIDLAQLJR | (11)

Since ψ˙ = ˙q4 and ˙s = ˙q5, we can rewrite eq.(7) as:

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
0 | A
− cos(ψ)(Py{a} + d3) | − sin(ψ)B
− sin(ψ)(Py{a} + d3) | cos(ψ)B
1 | 0
0 | − cos(ψ) LDALJQ LIDLAQLJR
0 | − sin(ψ) LDALJQ LIDLAQLJR

q˙4
q˙5
(12)

Because there is no rotation between the base frame {b} and the delta platform frame {p}, the velocity of the tool tip expressed in {b} is simply the sum of the delta platform’s velocity (in {b}) and the tool tip’s velocity in fixed {p} frame.

With that, we now have all the components needed to construct the Spatial Jacobian:

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
Jd[1,1] | Jd[1,2] | Jd[1,3] | 0 | A
Jd[2,1] | Jd[2,2] | Jd[2,3] | − cos(ψ)(Py{a} + d3) | − sin(ψ)B
Jd[3,1] | Jd[3,2] | Jd[3,3] | − sin(ψ)(Py{a} + d3) | cos(ψ)B
0 | 0 | 0 | 1 | 0
0 | 0 | 0 | 0 | − cos(ψ) LDALJQ LIDLAQLJR
0 | 0 | 0 | 0 | − sin(ψ) LDALJQ LIDLAQLJR

q˙1
q˙2
q˙3
q˙4
q˙5

(13)

Since ψ = q4, the Spatial Jacobian is:

Js =

Jd[1,1] | Jd[1,2] | Jd[1,3] | 0 | A
Jd[2,1] | Jd[2,2] | Jd[2,3] | − cos(q4)(Py{a} + d3) | − sin(q4)B
Jd[3,1] | Jd[3,2] | Jd[3,3] | − sin(q4)(Py{a} + d3) | cos(q4)B
0 | 0 | 0 | 1 | 0
0 | 0 | 0 | 0 | − cos(q4) LDALJQ LIDLAQLJR
0 | 0 | 0 | 0 | − sin(q4) LDALJQ LIDLAQLJR

(14)

### 3.3 Body Jacobian

Similar to the Spatial Jacobian, the Body Jacobian also maps joint velocities to the tool tip velocity, but expressed in the tool frame {t}.

x˙
y˙
z˙
˙θx
˙θy
˙θz

{t}

= Jb

q˙1
q˙2
q˙3
q˙4
q˙5

(15)

In the traditional formulation of robot kinematics, twists (which combine angular and linear velocity) are often used in conjunction with exponential coordinates and homogeneous transformation matrices. When switching between spatial and body frames, the adjoint transformation is typically applied as:

Vbody = Ad(T
−1
bt )Vspatial | (16)

where Ad(T
−1
bt )

is the adjoint matrix of the inverse transformation from the base frame {b} to the tool frame {t}. This standard adjoint takes both rotation and translation into account:

Ad(T) =

R 0

[p]R R
(17)

Here, R is the rotation matrix from one frame to another, p is the position vector between origins, and [p] is the skew-symmetric matrix of p.

However, in our case, we are not using twist representation or exponential coordinates directly. Instead, we are dealing with raw velocity vectors: stacked linear and angular velocity components in the form [v; ω]. These do not contain the full twist structure and lack the translational offset context needed for the full adjoint to apply correctly.

As such, the traditional adjoint would incorrectly mix rotational and translational effects when applied to our representation. To transform raw velocity vectors between frames, only the rotation part should be applied to each component separately. For example, vt = Rtbvb and ωt = Rtbωb.

Thus, we define a simplified adjoint-like mapping Ad†
(Ttb)

using only the rotation matrix:

Ad†
(Ttb) =
Rtb | 0
0 | Rtb
(18)

where Rtb = Rbt

T = Tbt[: 3, : 3]

T
, and Tbt is already been derived in eq.(4).

Finally, we get the expression of the Body Jacobian:

Jb = Ad†
(Ttb)Js | (19)

## 4 Jacobian Pseudo-inverse of SHER-3.0

In robotic kinematics, the Jacobian matrix J ∈ R

6×n maps joint velocities ˙q ∈ R
n
to end-effector
velocity v ∈ R

6
, and Jacobian inverse does the opposite thing as:

v = J ˙q

˙q = J

−1v

(20)

This works well when the number of joints n = 6, making J square and (if full rank) invertible. However, in our case, we only have 5 joints, so the Jacobian is a 6×5 matrix. That means it’s not directly invertible and no exact solution may exist for a general 6D velocity command.

To resolve this, we use the Moore-Penrose pseudo-inverse of the Jacobian, denoted J

† =
(J

T J)

−1J
T
, to find a least-squares optimal solution for the joint velocities ˙q that best approxi-mates the desired end-effector velocity:
˙q = J
†v | (21)

This gives us the joint velocity vector that minimizes the squared error between the actual and desired end-effector motion. It essentially ”projects” the 6D desired velocity into the 5D space of achievable motions.

### 4.1 Spatial Jacobian Pseudo-inverse

Since the Moore-Penrose pseudo-inverse is a general-purpose mathematical tool that can be applied to any non-square Jacobian matrix, it works for both Spatial and Body Jacobians.

Thus,
Js

† = (Js
T Js)

−1Js
T
(22)

˙q = Js

†vs | (23)

### 4.2 Body Jacobian Pseudo-inverse

Similarly,
Jb

† = (Jb
T Jb)

−1Jb
T
(24)

˙q = Jb

†vb | (25)

## 5 Validation with SolidWorks Motion Analysis

To validate the kinematic calculations presented in this document, I used SolidWorks to build a simplified CAD model of the SHER-3.0 mechanism. The assembly was constructed without incorporating any built-in kinematic constraints or control logic—only individual parts and their mechanical relationships were defined.

A motion simulation was then performed with SolidWorks Motion Study. Since SolidWorks Motion Simulation does not provide instantaneous velocity outputs at a specific configuration, I set the total simulation time to 0.5 seconds and observed the velocity values at time t=0.

At the initial moment, the model has not yet moved significantly, so the velocity at t=0 effec-tively represents the instantaneous velocity of the system at the given joint configuration. This allows for a valid comparison between the simulation results and the analytical velocity computed using the Jacobian-based method described in this document.

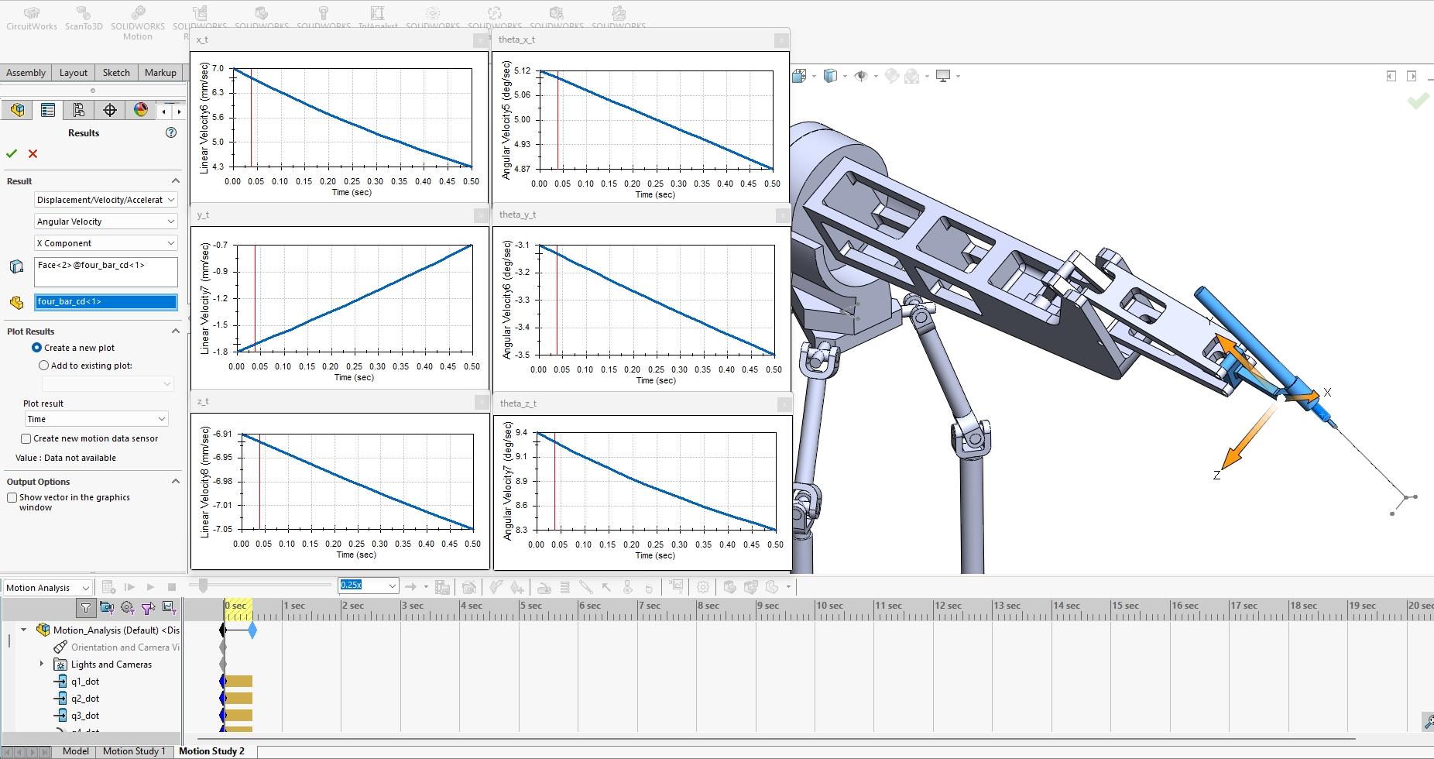
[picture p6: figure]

Figure 3: Motion Simulation Setup in SolidWorks

To test the model with arbitrary values, consider the following joint positions and velocities:

q1
q2
q3
q4
q5

=

1 mm
2 mm
3 mm
π
6

rad
10 mm

,

q˙1
q˙2
q˙3
q˙4
q˙5

=

4 mm/s
5 mm/s
6 mm/s
π
30 rad/s
10 mm/s

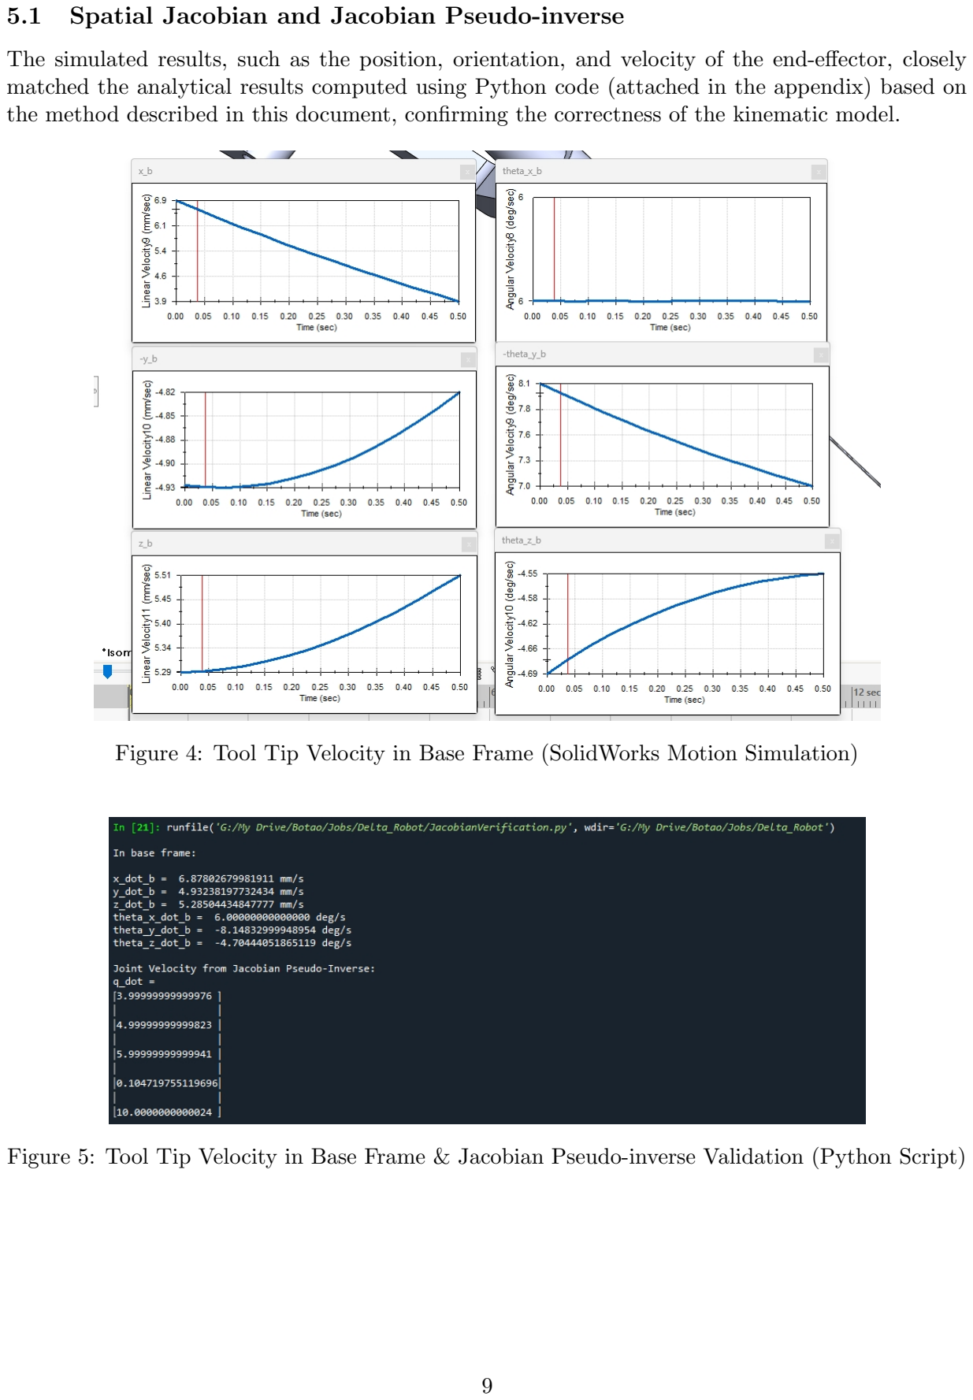
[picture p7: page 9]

### 5.1 Spatial Jacobian and Jacobian Pseudo-inverse

The simulated results, such as the position, orientation, and velocity of the end-effector, closely matched the analytical results computed using Python code (attached in the appendix) based on the method described in this document, confirming the correctness of the kinematic model.

Figure 4: Tool Tip Velocity in Base Frame (SolidWorks Motion Simulation)

Figure 5: Tool Tip Velocity in Base Frame & Jacobian Pseudo-inverse Validation (Python Script)

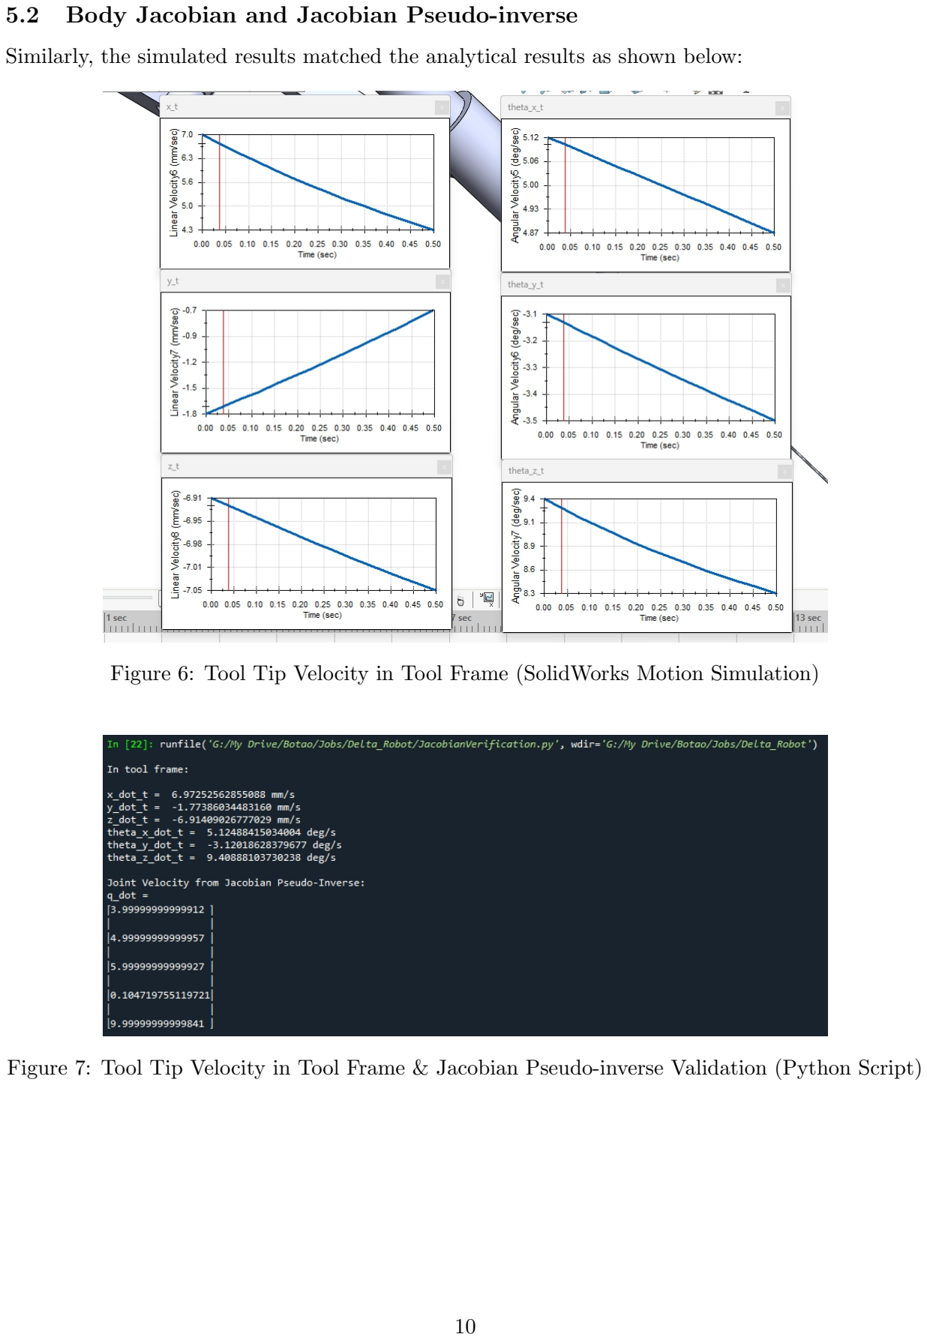
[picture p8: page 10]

### 5.2 Body Jacobian and Jacobian Pseudo-inverse

Similarly, the simulated results matched the analytical results as shown below:

Figure 6: Tool Tip Velocity in Tool Frame (SolidWorks Motion Simulation)

Figure 7: Tool Tip Velocity in Tool Frame & Jacobian Pseudo-inverse Validation (Python Script)

## 6 Disclaimer

The simulations and Jacobian-based calculations presented in this document are based on my personal understanding of the kinematic structure of SHER-3.0. Due to the complexity of the Jacobian—especially in systems involving multiple frames and mixed translational and rotational joints—there may be discrepancies between analytical results and simulation outputs. While the SolidWorks motion simulation validates the general correctness of the method, it is not guaranteed to match perfectly due to potential simplifications, numerical errors, or modeling assumptions. I encourage readers to focus on the methodology and reasoning behind the derivations rather than relying solely on the final equations. Please independently verify the results before applying them to any critical applications. If you spot any errors, have suggestions, or would like to discuss the topic further, feel free to reach out to me at: bzhao17@alumni.jh.edu.

## 7 Appendix: Python Scripts

### 7.1 Jacobian & Jacobian Pseudo-inverse Validation

1 | # -*- coding: utf-8 -*-
2 | """
3 | Created on Sun Jul 27 15:24:01 2025

4
5 | @author: Botao
6 | """

7
8 | import numpy as np
9 | from sympy import Matrix, zeros, pprint

10
11 | ################### Joint Parameters: ##############################
12 | q1 = 1 | # Prismatic
13 | q2 = 2 | # Prismatic
14 | q3 = 3 | # Prismatic
15 | q4 = 30*np.pi/180 | # Revolute
16 | q5 = 10 | # Prismatic

17
18 | ################### Joint Velocities: ##############################
19 | q1_dot = 4 | # mm/s
20 | q2_dot = 5 | # mm/s
21 | q3_dot = 6 | # mm/s
22 | q4_dot = 6*np.pi/180 | # rad/s
23 | q5_dot = 10 | # mm/s
24 | q_dot = Matrix([
25 | [q1_dot],
26 | [q2_dot],
27 | [q3_dot],
28 | [q4_dot],
29 | [q5_dot]
30 | ])

31
32 ################### Delta Platform: ###################################

33
34 | # Robot parameters
35 | rp = 34.4773 # mm platform radius
36 | rb = 60.6927 # mm base radius
37 | l = 68 | # mm rod length

38
39 | # Base joint angles
40 | theta1 = np.pi / 3
41 | theta2 = np.pi
42 | theta3 = 5 * np.pi / 3

43
44 | # Base joint positions (fixed)
45 | rb1 = np.array([np.cos(theta1)*rb, np.sin(theta1)*rb, 0])
46 | rb2 = np.array([np.cos(theta2)*rb, np.sin(theta2)*rb, 0])
47 | rb3 = np.array([np.cos(theta3)*rb, np.sin(theta3)*rb, 0])

48
49 | # Platform offsets (relative to center)
50 | rp1 = np.array([np.cos(theta1)*rp, np.sin(theta1)*rp, 0])
51 | rp2 = np.array([np.cos(theta2)*rp, np.sin(theta2)*rp, 0])
52 | rp3 = np.array([np.cos(theta3)*rp, np.sin(theta3)*rp, 0])

53

54
55 L1 = np.array([0,0,q1])

56 | L2 = np.array([0,0,q2])
57 | L3 = np.array([0,0,q3])

58
59 | e1 = L1 + rb1 - rp1
60 | e2 = L2 + rb2 - rp2
61 | e3 = L3 + rb3 - rp3

62
63 | h1 = ((e2[0]**2 + e2[1]**2 + e2[2]**2) - (e1[0]**2 + e1[1]**2 + e1[2]**2))/2
64 | h2 = ((e3[0]**2 + e3[1]**2 + e3[2]**2) - (e1[0]**2 + e1[1]**2 + e1[2]**2))/2

65
66 | x21 = (e2 - e1)[0]
67 | y21 = (e2 - e1)[1]
68 | z21 = (e2 - e1)[2]

69
70 | x31 = (e3 - e1)[0]
71 | y31 = (e3 - e1)[1]
72 | z31 = (e3 - e1)[2]

73
74 | k1 = (y31*z21/y21 - z31)/(x31 - y31*x21/y21)
75 | k2 = (h2 - y31*h1/y21)/(x31 - y31*x21/y21)
76 | k3 = (x31*z21/x21 - z31)/(y31 - x31*y21/x21)
77 | k4 = (h2 - x31*h1/x21)/(y31 - x31*y21/x21)

78
79 | T1 = k1**2 + k3**2 + 1
80 | T2 = k1*k2 + k3*k4 - e1[0]*k1 - e1[1]*k3 - e1[2]
81 | T3 = k2**2 + k4**2 -2*e1[0]*k2 - 2*e1[1]*k4 - l**2 + e1[0]**2 + e1[1]**2 + e1[2]**2

82
83 | z = (-T2 + np.sqrt(T2**2 - T1*T3))/T1
84 | x = k1*z + k2
85 | y = k3*z + k4

86
87 r = np.array([x, y, z])

88
89 | l1 = -L1 - rb1 + r + rp1
90 | l2 = -L2 - rb2 + r + rp2
91 | l3 = -L3 - rb3 + r + rp3

92

93
94 ################ Roll-Tilt Mechanism: ###########################

95
96 | s = q5
97 | s_dot = q5_dot
98 | psi = q4 # roll angle

99
100 | # Fixed Parameters
101 | x_AR_max = 60.48
102 | y_AR = -10
103 | L_AQ = 32.5
104 | L_QR = 42
105 | L_AB = 28
106 | L_BC = 78.5
107 | L_CD = 15
108 | L_DA = 73.5
109 | phi1 = np.pi / 2
110 | phi2 = np.pi * 138 / 180
111 | L_DP = 94.49
112 | phi3 = np.pi * 103.93 / 180
113 | phi4 = np.pi * 31.06 / 180
114 | L_T = 50

d1 = 56.01 # Distance between the center frame of the delta platform to point A d2 = 192.7
d3 = 25.5

# Angles in radians

phi1 = np.pi / 2
phi2 = np.pi * 138 / 180
phi3 = np.pi * 103.93 / 180 phi4 = np.pi * 31.06 / 180

# Position Analysis

x_AR = x_AR_max - s
L_AR = np.sqrt(x_AR**2 + y_AR**2)
alpha3 = np.arccos((L_AR**2 + L_AQ**2 - L_QR**2) / (2 * L_AR * L_AQ)) alpha4 = np.pi - np.arctan2(y_AR, -x_AR)
alpha = alpha3 + alpha4

theta1 = np.pi - (phi2 + alpha3 + alpha4)
alpha_1 = phi1 - theta1
L_BD = np.sqrt(L_AB**2 + L_DA**2 - 2 * L_AB * L_DA * np.cos(alpha_1)) beta_1 = np.arccos((L_AB**2 + L_BD**2 - L_DA**2) / (2 * L_AB * L_BD))

delta = np.arccos((L_CD**2 + L_BD**2 - L_BC**2) / (2 * L_CD * L_BD)) theta2 = phi1 + beta_1 - delta

# Velocity Analysis

L_JR = np.tan(alpha)*x_AR - y_AR
L_JQ = np.sqrt((L_JR+y_AR)**2 + x_AR**2) - L_AQ

rho_dot = s_dot / L_JR
theta1_dot = -L_JQ / L_AQ * rho_dot

beta_2 = np.arccos((L_BC**2 + L_BD**2 - L_CD**2) / (2 * L_BC * L_BD)) L_IA = L_AB * np.sin(beta_1 + beta_2) / np.sin(alpha_1 + beta_1 + beta_2) L_ID = L_IA - L_DA

theta2_dot = -L_DA / L_ID * theta1_dot

# Position in {a} frame:

px_a = np.cos(theta1)*L_DA + np.cos(theta2 - phi3)*L_DP py_a = np.sin(theta1)*L_DA + np.sin(theta2 - phi3)*L_DP

# Position in {p} frame:

px_p = px_a + d2
py_p = -np.sin(psi)*py_a - np.sin(psi)*d3 pz_p = np.cos(psi)*py_a + np.cos(psi)*d3 + d1

# Position in {b} frame:

px_b = px_a + d2 + x
py_b = -np.sin(psi)*py_a - np.sin(psi)*d3 + y pz_b = np.cos(psi)*py_a + np.cos(psi)*d3 + d1 + z

################## Spatial Jacobian ################

J_l = zeros(3,3)

J_l[0,0] = l1[0]
J_l[0,1] = l1[1]

J_l[0,2] = l1[2]
J_l[1,0] = l2[0]
J_l[1,1] = l2[1]
J_l[1,2] = l2[2]
J_l[2,0] = l3[0]
J_l[2,1] = l3[1]
J_l[2,2] = l3[2]

J_z = zeros(3,3)

J_z[0,0] = l1[2]
J_z[1,1] = l2[2]
J_z[2,2] = l3[2]

J_d = J_l.inv() * J_z

A = np.sin(theta1)*L_DA*L_JQ/(L_AQ*L_JR) - np.sin(theta2-phi3)*L_DP*L_DA*L_JQ/(L_ID*L_AQ*L_JR) B = -np.cos(theta1)*L_DA*L_JQ/(L_AQ*L_JR) + np.cos(theta2-phi3)*L_DP*L_DA*L_JQ/(L_ID*L_AQ*L_JR)

JacobianTip = zeros(6,5)

JacobianTip[:3, :3] = J_d

JacobianTip[1,3] = -np.cos(q4)*(py_a + d3) JacobianTip[2,3] = -np.sin(q4)*(py_a + d3) JacobianTip[3,3] = 1

JacobianTip[0,4] = A
JacobianTip[1,4] = -np.sin(q4)*B
JacobianTip[2,4] = np.cos(q4)*B
JacobianTip[4,4] = -np.cos(q4)*L_DA*L_JQ/(L_ID*L_AQ*L_JR) # Should there be a "-" in front? JacobianTip[5,4] = -np.sin(q4)*L_DA*L_JQ/(L_ID*L_AQ*L_JR)
208 | Js = JacobianTip | # 6x5 spatial Jacobian in base frame

################# Body Jacobian ###################

def adjoint_pseudo(T):
R = T[:3, :3]
return Matrix.vstack(
Matrix.hstack(R, Matrix.zeros(3)), Matrix.hstack(Matrix.zeros(3), R)

)

# Tbt is known

theta = np.pi/2 - phi4 - phi3 + theta2
Tbt = Matrix([
[np.cos(theta), -np.sin(theta), 0, px_a+d2+x],
[-np.sin(theta)*np.sin(psi), -np.cos(theta)*np.sin(psi), -np.cos(psi), -np.sin(psi)*py_a-np.sin(psi)*d3+y], [np.sin(theta)*np.cos(psi), np.cos(theta)*np.cos(psi), -np.sin(psi), np.cos(psi)*py_a+np.cos(psi)*d3+d1+z], [0, 0, 0, 1]
]) # 4x4 transformation from base to tool
Rbt = Tbt[:3, :3]

# Compute Ad_Tbt¹

Ttb = Tbt.inv()
Ad_Ttb = adjoint_pseudo(Ttb)

233
234 | # Compute body Jacobian
235 | Jb = Ad_Ttb * Js

236
237 | V_tool_t = Jb*q_dot
238 | V_tool_b = Js*q_dot

239
240 | # print("\nIn base frame:\n")
241 | # print("x_dot_b = ", V_tool_b[0], "mm/s")
242 | # print("y_dot_b = ", V_tool_b[1], "mm/s")
243 | # print("z_dot_b = ", V_tool_b[2], "mm/s")
244 | # print("theta_x_dot_b = ", V_tool_b[3]*180/np.pi, "deg/s")
245 | # print("theta_y_dot_b = ", V_tool_b[4]*180/np.pi, "deg/s")
246 | # print("theta_z_dot_b = ", V_tool_b[5]*180/np.pi, "deg/s\n")

247

248
249 | print("\nIn tool frame:\n")
250 | print("x_dot_t = ", V_tool_t[0], "mm/s")
251 | print("y_dot_t = ", V_tool_t[1], "mm/s")
252 | print("z_dot_t = ", V_tool_t[2], "mm/s")
253 | print("theta_x_dot_t = ", V_tool_t[3]*180/np.pi, "deg/s")
254 | print("theta_y_dot_t = ", V_tool_t[4]*180/np.pi, "deg/s")
255 | print("theta_z_dot_t = ", V_tool_t[5]*180/np.pi, "deg/s\n")

256

257

258
259 ################ Jacobian Inverse ##################

260
261 | Js_pseudo_inv = (Js.T * Js).inv() * Js.T
262 | Jb_pseudo_inv = (Jb.T * Jb).inv() * Jb.T

263
264 | q_dot_verify_s = Js_pseudo_inv * V_tool_b
265 | q_dot_verify_b = Jb_pseudo_inv * V_tool_t

266
267 | print("Joint Velocity from Jacobian Pseudo-Inverse:")
268 | print("q_dot =")
269 | pprint(q_dot_verify_s) # The results should match your q_dot values

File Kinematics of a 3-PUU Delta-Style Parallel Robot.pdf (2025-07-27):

## Kinematics of a 3-PUU Delta-Style Parallel Robot

Botao Zhao

June 12, 2025

## Contents

1 Introduction | 2
2 System Overview | 2
3 Inverse Kinematics | 4
4 Forward Kinematics | 5
5 Delta Platform Jacobian | 7
6 Kinematics Simulation and Visualization | 9
7 Disclaimer | 9
8 Appendix: Python Scripts | 10

## 1 Introduction

The purpose of this document is to give a quick understand of the kinematics of the delta platfrom of SHER-3.0 (Eye Robor 3.0) to those who are new to this project. It is assumed the reader has already taken the course RDKDC and familiar with some basic robotics and linear algebra knowledge. Some related papers and scripts can be found on this github page: https://github.com/zhaob5/delta_kinematics (https://github.com/zhaob5/delta_kinematics)

## 2 System Overview

The Delta platform is a parallel manipulator known for high speed and accuracy, commonly used in pick-and-place applications. This tutorial focuses on a variation with a 3-PUU configuration, where each leg consists of a vertical Pristmatic actuator (active joint), and followed by two passive Universal joints.

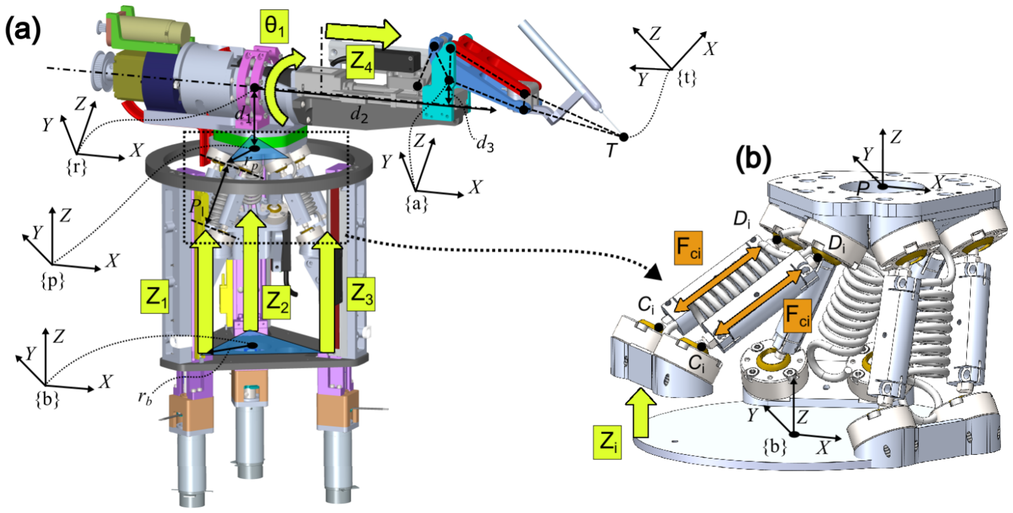
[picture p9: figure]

Figure 1: CAD models of (a) SHER-3.0, and (b) close up of the delta platform

We assume three identical legs connecting the base and moving platform, forming a closed kinematic loop.

### 2.1 Assumptions and Parameters

- Base joint circle radius: rb
- Platform joint circle radius: rp
- Angle between prismatic joint to base frame’s x-axis: θbi ∈
π
3

, π, 5π
3
- Angle between upper universal joint to moving frame’s x-axis: θpi ∈
π
3

, π, 5π
3
- Link length between universal joints: l
- Vector form of link: li = [xli
, yli
, zli

]

T

- Vector form of prismatic joint: Li = [0, 0, qi ]

T

- End-effector position: r = [x, y, z]
T

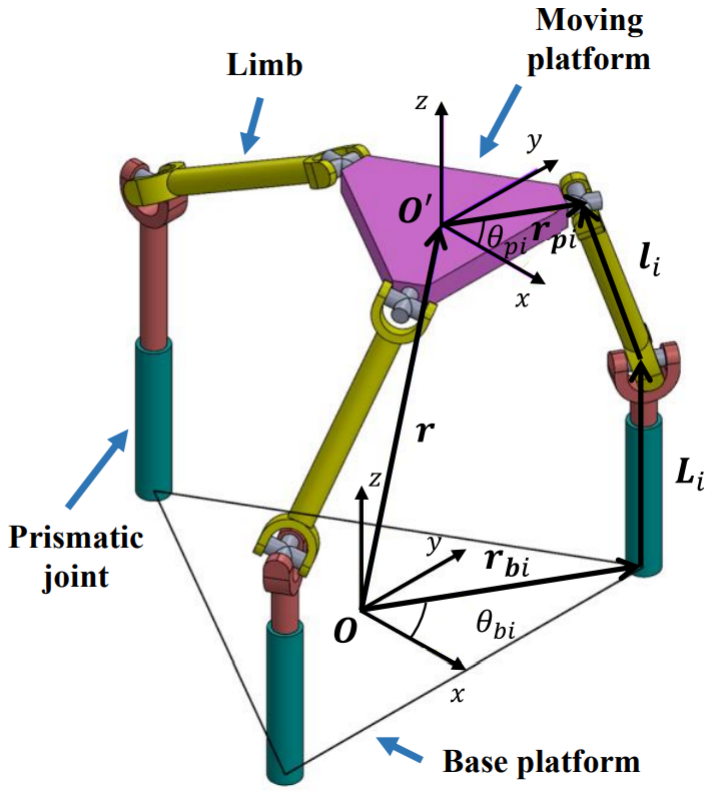
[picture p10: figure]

Figure 2: Simplified 3-D view of the delta platform.

## 3 Inverse Kinematics

For a closed-chain robot, the inverse kinematics is relatively straightforward to derive from its geometry or vector loop equations. Given a desired end-effector position r = [x, y, z]

T
, the task is
to compute the required lengths of the prismatic actuators qi for i = 1, 2, 3.

### 3.1 Vector Loop

As shown in Fig.2, the nominal length of the limbs is li . The joint length of each prismatic joints is qi

. The i−th vector loop closure equation is given by:

li = −Li − rbi + r + rpi | (1)

where Li = [0, 0, qi

]

T

, rbi = [rbi cos θbi, rbi cos θbi, 0]T and rpi = [rpi cos θpi, rpi cos θpi, 0]T .

### 3.2 Inverse Kinematics Equations

Write eq.(1) in matrix form:

xli
yli
zli
- = −

0
0
qi
- −

rb cos(θi)
rb sin(θi)
0
- +

x
y
z
- +

rp cos(θi)
rp sin(θi)
0
- (2)

Since the length of each link is l =

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
, eq.(2) can be written as:

x

2
li + y

2
li + z

2
li = l

2 = (x + ai)

2 + (y + bi)

2 + (z − qi)

2
(3)

where ai and bi are just two constants: ai = −rb cos θi + rp cos θi

, bi = −rb sin θi + rp sin θi Reorganize eq.(3), we can get:

qi = z −

p
l

2 − (x + ai)

2 − (y + bi)

2 | (4)

This gives the prismatic actuator extension for each leg, where i = 1, 2, 3.

## 4 Forward Kinematics

Unlike serial robots (e.g., the UR5), the forward kinematics of a closed-chain robot is typically much harder to compute and can have multiple solutions. For example, if you try to directly substitute the known actuator values qi back into eq.(3), you’ll find that the resulting equations are coupled through x,y,z. The expressions contain quadratic cross-terms, making the system nonlinear and often analytically intractable. Additionally, multiple valid solutions exist, further complicating the problem.
The method described in this document uses some linear algebra tricks to eliminate as many of the quadratic cross-terms as possible. It may not be the most efficient or elegant way to solve forward kinematics for this delta platform. If you have a better idea or approach, feel free to improve this document by adding your method.

### 4.1 Rearranging the Vector Loop Equation

Since Li

, rbi, rpi are known, we can define ei = Li + rbi − rpi and rewrite eq.(1) as:

li = r − ei | (5)

Then, dot-multiplying eq.(5) with itself on both side (rememebr a · b = a

Tb):

l

T
i

li = (r − ei)

T
(r − ei) | (6)

l

2 = r

T
r − 2r

T
ei + e

T
i ei | (7)

From eq.(7), we can get three equations for i =1, 2, 3:

l

2 = r

T
r − 2r

T
e1 + e

T
1 e1 | (8)

l

2 = r

T
r − 2r

T
e2 + e

T
2 e2 | (9)

l

2 = r

T
r − 2r

T
e3 + e

T
3 e3 | (10)

Subtracting eq.(8) with eq.(9) and eq.(10) respectively, we will get:

0 = −2r

T
(e2 − e1) + (e

T
2 e2 − e

T
1 e1) | (11)

0 = −2r

T
(e3 − e1) + (e

T
3 e3 − e

T
1 e1) | (12)

Let h1 = (e

T
2

e2 − e

T
1

e1)/2 and h2 = (e

T
3

e3 − e

T
1

e1)/2, rearranging eq.(11) and eq.(12):

r

T
(e2 − e1) − h1 = 0 | (13)

r

T
(e3 − e1) − h2 = 0 | (14)

### 4.2 Forward Kinematics Equations

Since all of the elements in (e2 − e1) and (e3 − e1) are constants, let e2 − e1 = [x21, y21, z21]

T and

e3 − e1 = [x31, y31, z31]

T
. Then eq.(13) and eq.(14) can be expressed as:
x y z

x21

y21

z21

- − h1 = 0 | (15)

x y z

x31

y31

z31

- − h2 = 0 | (16)

Then we get two equations with three unknowns x, y, z:

x21x + y21y + z21z − h1 = 0 | (17)
x31x + y31y + z31z − h2 = 0 | (18)

Rearranging eq.(17) and eq.(18):

x =

(y31z21/y21 − z31)

(x31 − y31x21/y21)

z +

(h2 − y31h1/y21)

(x31 − y31x21/y21)

(19)

y =

(x31z21/x21 − z31)

(y31 − x31y21/x21)

z +

(h2 − x31h1/x21)

(y31 − x31y21/x21)

(20)

Let k1 =

(y31z21/y21−z31)
(x31−y31x21/y21)

, k2 =

(h2−y31h1/y21)
(x31−y31x21/y21)

, k3 =

(x31z21/x21−z31)
(y31−x31y21/x21)

, k4 =

(h2−x31h1/x21)
(y31−x31y21/x21)

Then substituting eq.(19) and eq.(20) into eq.(8), where e1 = [e1x, e1y, e1z]

T
:

l

2 =

k1z + k2 | k3z + k4 | z

k1z + k2
k3z + k4
z
- − 2
k1z + k2 | k3z + k4 | z

e1x

e1y

e1z

- + e

T
1 e1 (21)

Rearranging eq.(21):

z =

−T2 ±

p
T

2
2 − T1T3
T1

(22)

where T1 = k

2
1 + k

2
3 + 1, T2 = k1k2 + k3k4 − e1xk1 − e1yk3 − e1z, and T3 = k

2
2 + k

2
4 − 2e1xk2 − 2e1yk4 − l

2 + e

2
1x + e

2
1y + e

2
1z

Since the delta platform must be above the base plane, when there are two different real solutions, only the one with positive z value is valid.

Thus, eq.(19), eq.(20), and eq.(22) represent the forward kinematic solutions.

## 5 Delta Platform Jacobian

Let r˙ = [ ˙x, y,˙ z˙]

T be the end-effector (delta platform) velocity, and L˙ i = [0, 0, q˙i

]

T
the rate of change
of each prismatic joint.

Rearranging eq.(1) and taking derivative to both side:

L˙

i = r˙ − ˙
li − r˙ bi + r˙ pi | (23)

Since all of the elements in rbi and rpi are constants, r˙ bi = r˙ pi = 0.

Thus,

L˙

i = r˙ − ˙
li | (24)

### 5.1 Time Derivative of Position Vector

Assuming we have a moving vector from point A to point B, l = B − A, as shown below:

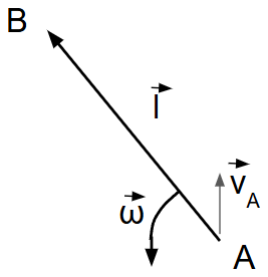
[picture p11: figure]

Figure 3: A moving vector l.

Point A is moving at speed vA and the vector itself has an angular velocity ω. The length of this vector is unchanged. The velocity of point B is:

vB = vA + ω × l

Then:

vB − vA = ω × l

B˙ − A˙ = ω × l

Thus,

˙
l = ω × l

The time derivative of this moving vector is the angular velocity cross product itself.

### 5.2 Jacobian Matrix Derivation

Known the result of ˙
l = ω × l, we can rewrite eq.(24) as:

L˙
i = r˙ − (ωi × li) | (25)

Dot-multiplying li to both side:

li

- L˙
i = li
- r˙ − li
- (ωi × li) | (26)

Since li

is perpendicular to ωi × li

, and a · b = a

Tb:

l

T

i L˙
i = l

T
i
r˙ | (27)
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
- (28)

zli

q˙i = xlix˙ + yli

y˙ + zli

z˙ | (29)

expand eq.(29) with i = 1, 2, 3:

zl1

| 0 | 0
0 | zl2 | 0
0 | 0 | zl3

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
- (30)

Thus we can obtain:

r˙ = Jq˙ | (31)

q˙ = J

−1
r˙ | (32)

where

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
| 0 | 0
0 | zl2 | 0
0 | 0 | zl3
- (33)

is the 3×3 Jacobian matrix of the delta platform.

## 6 Kinematics Simulation and Visualization

This work is part of my personal project, which is available on https://github.com/zhaob5/delta_kinematics. (https://github.com/zhaob5/delta_kinematics) So far, it includes only the inverse and forward kinematics of the simulation. I plan to expand it with Jacobian analysis, and full SHER-3.0 visualization in the future, if time permitting. Feel free to follow the page for updates or contribute if you’re interested.

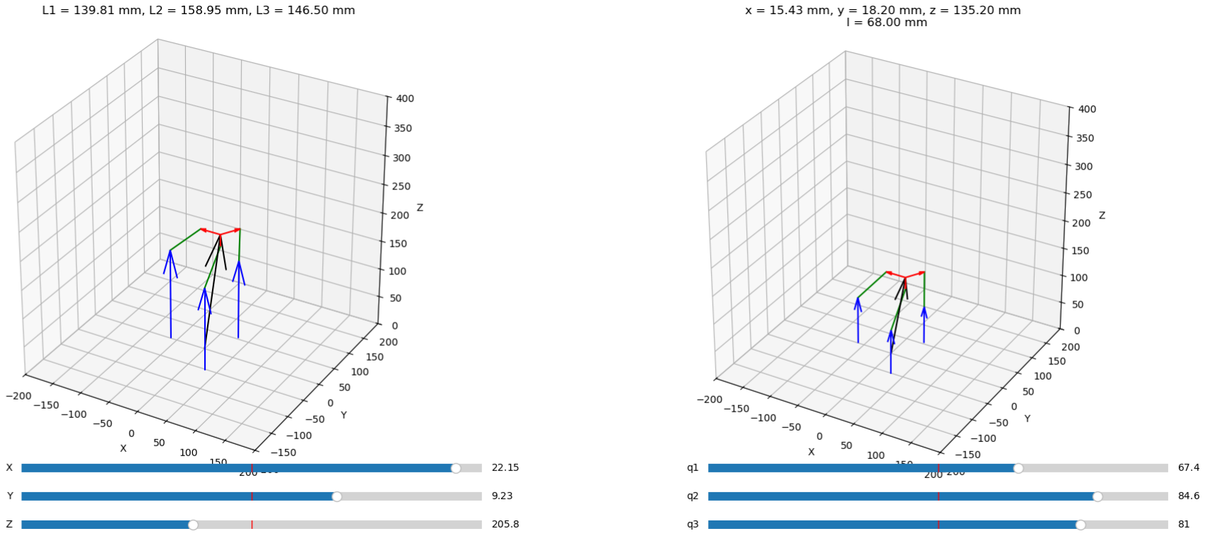
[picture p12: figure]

Figure 4: Inverse Kinematics Visualization Figure 5: Forward Kinematics Visualization

## 7 Disclaimer

The calculations and methods presented in this document are based on my personal understanding and interpretation of the kinematics of closed-chain robots. While I’ve made every effort to ensure accuracy, there may still be errors or oversights. I strongly encourage you to verify the results independently before applying them in any critical context. If you have suggestions, corrections, or would like to discuss the topic further, feel free to reach out to me at: bzhao17@alumni.jh.edu.

## 8 Appendix: Python Scripts

### 8.1 Inverse Kinematics Visualization

# # -*- coding: utf-8 -*-

"""
SHER-3.0 Delta Inverse Kinematics Visualization

Created on Wed Jun 11 17:11:23 2025

@author: Botao Zhao
"""
import numpy as np
import matplotlib.pyplot as plt
from matplotlib.widgets import Slider import matplotlib.gridspec as gridspec

# Robot parameters

rp = 34.4773 # mm platform radius
rb = 60.6927 # mm base radius
17 | l = 68 | # mm rod length

# Base joint angles

theta1 = np.pi / 3
theta2 = np.pi
theta3 = 5 * np.pi / 3

# Base joint positions (fixed)

rb1 = np.array([np.cos(theta1)*rb, np.sin(theta1)*rb, 0]) rb2 = np.array([np.cos(theta2)*rb, np.sin(theta2)*rb, 0]) rb3 = np.array([np.cos(theta3)*rb, np.sin(theta3)*rb, 0])

# Platform offsets (relative to center)

rp1 = np.array([np.cos(theta1)*rp, np.sin(theta1)*rp, 0]) rp2 = np.array([np.cos(theta2)*rp, np.sin(theta2)*rp, 0]) rp3 = np.array([np.cos(theta3)*rp, np.sin(theta3)*rp, 0])

def calculate_actuator_lengths(x, y, z):
# Platform joint positions in world frame

p1 = np.array([x, y, z]) + rp1
p2 = np.array([x, y, z]) + rp2
p3 = np.array([x, y, z]) + rp3

# Vectors from base to platform joints l1 = p1 - rb1

l2 = p2 - rb2
l3 = p3 - rb3

# z_i = z - sqrt(l^2 - dx^2 - dy^2) def z_offset(vec):

| | dx, dy = vec[0], vec[1] d_squared = dx**2 + dy**2 if d_squared > l**2: return np.nan

51 | return z - np.sqrt(l**2 - d_squared)

52
53 | z1 = z_offset(l1)
54 | z2 = z_offset(l2)
55 | z3 = z_offset(l3)

56
57 | return z1, z2, z3

58
59 | def update(val):
60 | x = slider_x.val
61 | y = slider_y.val
62 | z = slider_z.val

63
64 | z1, z2, z3 = calculate_actuator_lengths(x, y, z)

65
66 | ax.cla()

67
68 | # Replot everything
69 | p1 = np.array([x, y, z]) + rp1
70 | p2 = np.array([x, y, z]) + rp2
71 | p3 = np.array([x, y, z]) + rp3

72
73 | # l1 = [p1[0] - rb1[0], p1[1] - rb1[1], z1]
74 | # l2 = [p2[0] - rb2[0], p2[1] - rb2[1], z2]
75 | # l3 = [p3[0] - rb3[0], p3[1] - rb3[1], z3]

76
77 | # links
78 | ax.plot([rb1[0], p1[0]], [rb1[1], p1[1]], [rb1[2] + z1, p1[2]], 'g')
79 | ax.plot([rb2[0], p2[0]], [rb2[1], p2[1]], [rb2[2] + z2, p2[2]], 'g')
80 | ax.plot([rb3[0], p3[0]], [rb3[1], p3[1]], [rb3[2] + z3, p3[2]], 'g')

81
82 | ax.quiver(rb1[0], rb1[1], rb1[2], 0, 0, z1, color='b')
83 | ax.quiver(rb2[0], rb2[1], rb2[2], 0, 0, z2, color='b')
84 | ax.quiver(rb3[0], rb3[1], rb3[2], 0, 0, z3, color='b')

85
86 | ax.quiver(0, 0, 0, x, y, z, color='k')

87
88 | # Platform vectors
89 | ax.quiver(x, y, z, rp1[0], rp1[1], rp1[2], color='r')
90 | ax.quiver(x, y, z, rp2[0], rp2[1], rp2[2], color='r')
91 | ax.quiver(x, y, z, rp3[0], rp3[1], rp3[2], color='r')

92
93 | ax.set_xlim([-200, 200])
94 | ax.set_ylim([-200, 200])
95 | ax.set_zlim([0, 400])
96 | ax.set_box_aspect([1, 1, 1])
97 | ax.set_xlabel("X")
98 | ax.set_ylabel("Y")
99 | ax.set_zlabel("Z")
100 | ax.set_title(f"L1 = {z1:.2f} mm, L2 = {z2:.2f} mm, L3 = {z3:.2f} mm")

101
102 | fig.canvas.draw_idle()

103
104 # Initial pose

105 x0, y0, z0 = 0, 0, 225

106
107 | # Set up figure with space for sliders
108 | fig = plt.figure(figsize=(10, 8))
109 | gs = gridspec.GridSpec(2, 1, height_ratios=[6, 1])
110 | ax = fig.add_subplot(gs[0], projection='3d')

111
112 | slider_ax_x = plt.axes([0.25, 0.15, 0.65, 0.03])
113 | slider_ax_y = plt.axes([0.25, 0.10, 0.65, 0.03])
114 | slider_ax_z = plt.axes([0.25, 0.05, 0.65, 0.03])

115
116 | slider_x = Slider(slider_ax_x, 'X', -25, 25, valinit=x0)
117 | slider_y = Slider(slider_ax_y, 'Y', -25, 25, valinit=y0)
118 | slider_z = Slider(slider_ax_z, 'Z', 150, 300, valinit=z0)

119
120 | # Hook update
121 | slider_x.on_changed(update)
122 | slider_y.on_changed(update)
123 | slider_z.on_changed(update)

124
125 | # Initial draw
126 | update(None)
127 | plt.tight_layout()
128 | plt.show()

### 8.2 Forward Kinematics Visualization

# -*- coding: utf-8 -*-

"""
Created on Wed Jun 11 21:13:48 2025

@author: Botao
"""

import numpy as np
import matplotlib.pyplot as plt
from matplotlib.widgets import Slider import matplotlib.gridspec as gridspec

# Robot parameters

rp = 34.4773 # mm platform radius
rb = 60.6927 # mm base radius
16 | l = 68 | # mm rod length

# Base joint angles

theta1 = np.pi / 3
theta2 = np.pi
theta3 = 5 * np.pi / 3

# Base joint positions (fixed)

rb1 = np.array([np.cos(theta1)*rb, np.sin(theta1)*rb, 0]) rb2 = np.array([np.cos(theta2)*rb, np.sin(theta2)*rb, 0]) rb3 = np.array([np.cos(theta3)*rb, np.sin(theta3)*rb, 0])

# Platform offsets (relative to center)

rp1 = np.array([np.cos(theta1)*rp, np.sin(theta1)*rp, 0]) rp2 = np.array([np.cos(theta2)*rp, np.sin(theta2)*rp, 0]) rp3 = np.array([np.cos(theta3)*rp, np.sin(theta3)*rp, 0])

def update(val):
q1 = slider_q1.val
q2 = slider_q2.val
q3 = slider_q3.val

L1 = np.array([0,0,q1])
L2 = np.array([0,0,q2])
L3 = np.array([0,0,q3])

e1 = L1 + rb1 - rp1
e2 = L2 + rb2 - rp2
e3 = L3 + rb3 - rp3

h1 = ((e2[0]**2 + e2[1]**2 + e2[2]**2) - (e1[0]**2 + e1[1]**2 + e1[2]**2))/2 h2 = ((e3[0]**2 + e3[1]**2 + e3[2]**2) - (e1[0]**2 + e1[1]**2 + e1[2]**2))/2

x21 = (e2 - e1)[0]
y21 = (e2 - e1)[1]
z21 = (e2 - e1)[2]

53 | x31 = (e3 - e1)[0]
54 | y31 = (e3 - e1)[1]
55 | z31 = (e3 - e1)[2]

56
57 | k1 = (y31*z21/y21 - z31)/(x31 - y31*x21/y21)
58 | k2 = (h2 - y31*h1/y21)/(x31 - y31*x21/y21)
59 | k3 = (x31*z21/x21 - z31)/(y31 - x31*y21/x21)
60 | k4 = (h2 - x31*h1/x21)/(y31 - x31*y21/x21)

61
62 | T1 = k1**2 + k3**2 + 1
63 | T2 = k1*k2 + k3*k4 - e1[0]*k1 - e1[1]*k3 - e1[2]
64 | T3 = k2**2 + k4**2 -2*e1[0]*k2 - 2*e1[1]*k4 - l**2 + e1[0]**2 + e1[1]**2 + e1[2]**2

65
66 | z = (-T2 + np.sqrt(T2**2 - T1*T3))/T1
67 | x = k1*z + k2
68 | y = k3*z + k4

69
70 | l1 = np.array([x, y, z]) - e1

71
72 | ax.cla()

73
74 | # Replot everything
75 | p1 = np.array([x, y, z]) + rp1
76 | p2 = np.array([x, y, z]) + rp2
77 | p3 = np.array([x, y, z]) + rp3

78
79 | # l1 = [p1[0] - rb1[0], p1[1] - rb1[1], z1]
80 | # l2 = [p2[0] - rb2[0], p2[1] - rb2[1], z2]
81 | # l3 = [p3[0] - rb3[0], p3[1] - rb3[1], z3]

82
83 | # links
84 | ax.plot([rb1[0], p1[0]], [rb1[1], p1[1]], [rb1[2] + q1, p1[2]], 'g')
85 | ax.plot([rb2[0], p2[0]], [rb2[1], p2[1]], [rb2[2] + q2, p2[2]], 'g')
86 | ax.plot([rb3[0], p3[0]], [rb3[1], p3[1]], [rb3[2] + q3, p3[2]], 'g')

87
88 | ax.quiver(rb1[0], rb1[1], rb1[2], 0, 0, q1, color='b')
89 | ax.quiver(rb2[0], rb2[1], rb2[2], 0, 0, q2, color='b')
90 | ax.quiver(rb3[0], rb3[1], rb3[2], 0, 0, q3, color='b')

91
92 | ax.quiver(0, 0, 0, x, y, z, color='k')

93
94 | # Platform vectors
95 | ax.quiver(x, y, z, rp1[0], rp1[1], rp1[2], color='r')
96 | ax.quiver(x, y, z, rp2[0], rp2[1], rp2[2], color='r')
97 | ax.quiver(x, y, z, rp3[0], rp3[1], rp3[2], color='r')

98
99 | ax.set_xlim([-200, 200])
100 | ax.set_ylim([-200, 200])
101 | ax.set_zlim([0, 400])
102 | ax.set_box_aspect([1, 1, 1])
103 | ax.set_xlabel("X")
104 | ax.set_ylabel("Y")
105 | ax.set_zlabel("Z")
106 | ax.set_title(f"x = {x:.2f} mm, y = {y:.2f} mm, z = {z:.2f} mm \n l = {np.linalg.norm(l1):.2f} mm")

107
108 | fig.canvas.draw_idle()

109
110 | # Initial pose
111 | q10, q20, q30 = 50, 50, 50

112
113 | # Set up figure with space for sliders
114 | fig = plt.figure(figsize=(10, 8))
115 | gs = gridspec.GridSpec(2, 1, height_ratios=[6, 1])
116 | ax = fig.add_subplot(gs[0], projection='3d')

117
118 | slider_ax_q1 = plt.axes([0.25, 0.15, 0.65, 0.03])
119 | slider_ax_q2 = plt.axes([0.25, 0.10, 0.65, 0.03])
120 | slider_ax_q3 = plt.axes([0.25, 0.05, 0.65, 0.03])

121
122 | slider_q1 = Slider(slider_ax_q1, 'q1', 0, 100, valinit=q10)
123 | slider_q2 = Slider(slider_ax_q2, 'q2', 0, 100, valinit=q20)
124 | slider_q3 = Slider(slider_ax_q3, 'q3', 0, 100, valinit=q30)

125
126 | # Hook update
127 | slider_q1.on_changed(update)
128 | slider_q2.on_changed(update)
129 | slider_q3.on_changed(update)

130
131 | # Initial draw
132 | update(None)
133 | plt.tight_layout()
134 | plt.show()

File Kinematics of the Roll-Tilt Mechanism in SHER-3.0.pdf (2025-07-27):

## Kinematics of the Roll-Tilt Mechanism in SHER-3.0

Botao Zhao

July 26, 2025

## Contents

1 Introduction | 2
2 System Overview | 2
3 Four-Bar Linkage Mechanism | 3
4 Roll Mechanism | 8
5 Tool Tip Velocity in Delta Platform Frame | 9
6 Kinematics Simulation and Visualization | 11
7 Disclaimer | 11
8 Appendix: Python Scripts | 12

## 1 Introduction

The purpose of this document is to provide a quick and accessible understanding of the roll and tilt mechanism of SHER-3.0 (Eye Robot 3.0). It is assumed that the reader is already familiar with some basic engineering kinematics, robotics, and linear algebra concepts. A separate document covering the kinematic derivation of the delta platform is also available at https://github.com/zhaob5/delta_kinematics. (https://github.com/zhaob5/delta_kinematics) If you haven’t read it yet, I strongly encourage you to review it before diving into this document, as some explanations here build upon concepts introduced there. Some related papers and scripts can be found on this github page: https://github.com/zhaob5/roll_tilt_mechanism (https://github.com/zhaob5/roll_tilt_mechanism)

## 2 System Overview

The base of SHER-3.0 is a delta mechanism, which has been described in detail in my previous work. Mounted on top of the delta stage is a 2-DOF arm with roll and tilt functionality. The tilt mechanism was designed with a four-bar linkage configuration, as illustrated in Fig.(1) and Fig.(2).

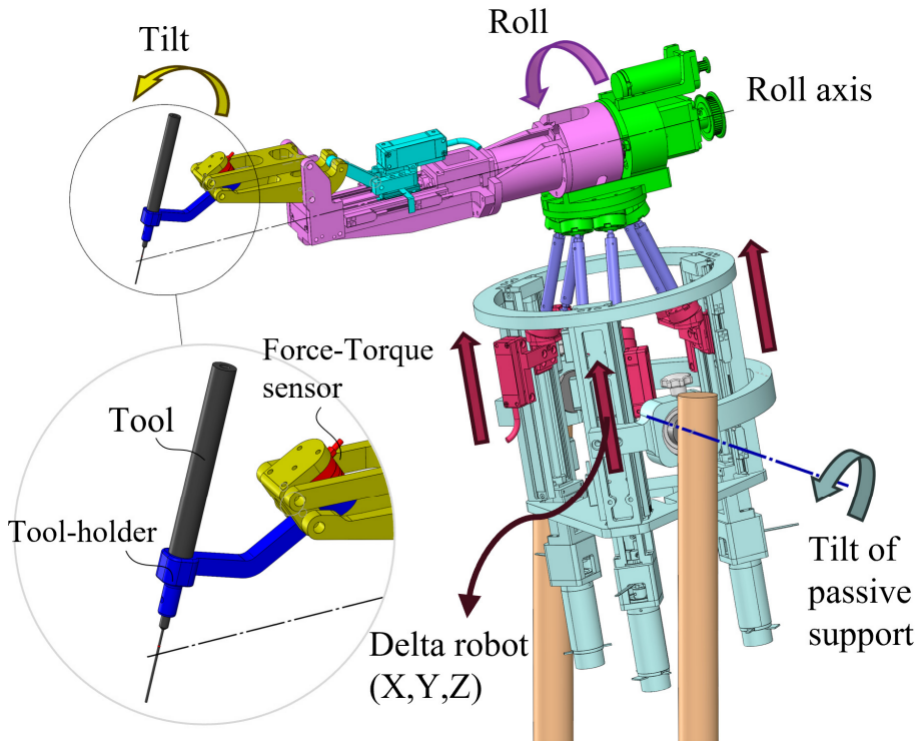
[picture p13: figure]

Figure 1: CAD models of the 5-DOF delta and roll-tilt mechanism

### 2.1 Tilting Mechanism

The structure of the tilt mechanism is depicted in Fig.(2). The joints A, B, C and D form a four-bar linkage mechanism. The joints A and B are fixed to the robot arm. This mechanism is actuated by an offset slider-crank mechanism with joints R, Q and A, where joint R is moved by a linear actuator. The rigid three-joint link QAD transfers the motion from the slider-crank to the four-bar. A tool-holder is mechanically fixed to the link CD and defines the offset towards the point P, which is the intended primary location for the RCM of the tool.
Since a four-bar mechanism cannot provide a mechanically enforced RCM, the point P shifts as the tool tilts. However, this motion can be actively compensated using the delta robot’s degrees of freedom, thereby enabling a virtual RCM (V-RCM) despite the lack of a mechanically enforced pivot.

## 3 Four-Bar Linkage Mechanism

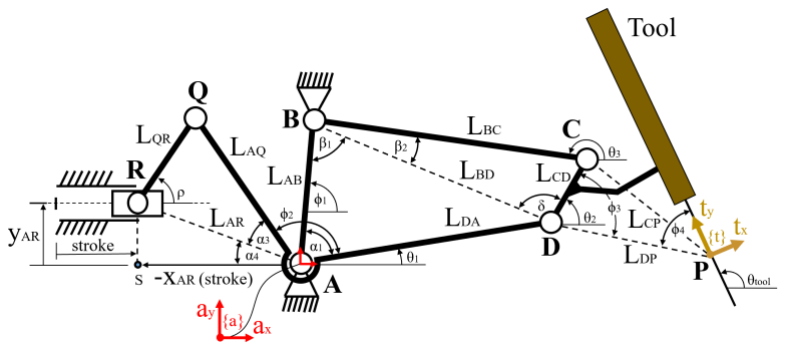
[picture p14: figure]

Figure 2: Side view of the tilt mechanism

### 3.1 Forward Kinematics

For the forward kinematics of this four-bar mechanism, the input is the linear actuator stroke length s, and the output is the tool angle θtool. Due to the nature of the four-bar linkage, the motion of the tool involves both rotation and translation. However, these two motions are kinematically coupled — knowing one uniquely determines the other.
The forward kinematics is relatively straightforward to compute since the lengths of all the links are known. Link AB is fixed in space, and point P maintains a fixed position relative to link CD. For simplicity, we define point A as the origin of the coordinate system. As the stroke length s ∈ [0, 50] is known:
xAR = xARmax − s | (1)

where xARmax

is the max horizontal distance between the origin to the slider, which is known based on the design parameter, and yAR is also a fixed value, representing the height from the linear guide rail to the frame {a}.

Thus,

LAR =

q
x

2
AR + y

2
AR | (2)
α4 = arctan (yAR, xAR) | (3)

As the lengths of AQ and QR are know, we can get α3 from the law of cosine:

α3 = arccos (

L

2
AR + L

2
AQ − L

2
QR
2LARLAQ
) | (4)

Since ϕ1 and ϕ2 are angles with fixed values, and α3, α4 are known:

θ1 = 180◦ − (ϕ2 + α3 + α4) | (5)
α1 = ϕ1 − θ1 | (6)

Form the law of cosine again:

LBD =

q
L

2
AB + L

2
DA − 2LABLDA cos(α1) | (7)

β1 = arccos (L

2
AB + L

2
BD − L

2
DA
2LABLBD
) | (8)

δ = arccos (L

2
BD + L

2
CD − L

2
BC
2LBDLCD
) | (9)
θ2 = 180◦ − ((180◦ − β1 − ϕ1) + δ) = β1 + ϕ1 − δ | (10)

Since ϕ3 and ϕ4 are also known:

θtool = 180◦ − ϕ4 − (ϕ3 − θ2) | (11)

As the lengths of AD and DP are constants, the x and y coordinates of point P in frame {a} can be directly computed:

Px = cos(θ1)LDA + cos(θ2 − ϕ3)LDP | (12)
Py = sin(θ1)LDA + sin(θ2 − ϕ3)LDP | (13)

To express the transformation matrix from coordinate frame {a} to {t}, we can adopt a simpli-fied approach by modeling links AD and DP as a 2-DOF serial robotic arm, but it is important to note that the joint angles in this representation are not independent.

Let θ = 90◦ − ϕ4 − (ϕ3 − θ2), the angle between the x-axis of frame {a} and the x-axis of frame {t}:

Tat =

cos(θ) − sin(θ) 0 Px
sin(θ) | cos(θ) | 0 Py
0 | 0 | 1 | 0
0 | 0 | 0 | 1

(14)

Thus, given the stroke length s, we can then determine both the tool’s tilt angle and its position relative to frame {a}.

### 3.2 Inverse Kinematics

The inverse kinematics of this mechanism is somewhat more complex. Given the tool’s tilt angle θtool, we can determine θ2. However, if you substitute θ2 back to the eq.(10) to compute θ1, you will find that both β1 and δ are unknown since the length of BD is also unknown. Solving for these variables would require handling a set of quadratic equations, which can be computationally expensive.
Thus, a more efficient approach is to derive the inverse kinematics directly from the geometry of the four-bar linkage. By translating edges AB and BC to form a new quadrilateral ABCE, as shown in Fig.(3):

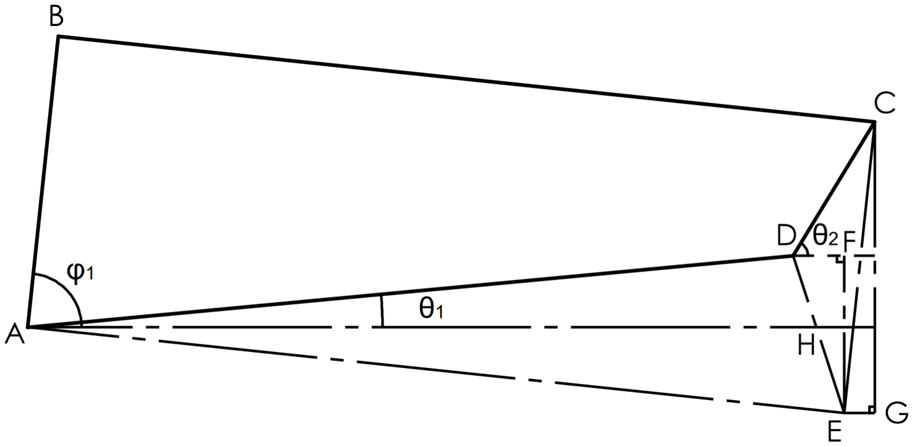
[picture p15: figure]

Figure 3: Close up of the four-bar mechanism

The goal is to determine the stroke length s given the value of θ2:

We know that LCE = LAB, LAE = LBC, ∠CEG = ϕ1

LDF = cos(θ2)LCD − cos(ϕ1)LAB | (15)
LEF = sin(ϕ1)LAB − sin(θ2)LCD | (16)

LDE =

q
L

2
DF + L

2
EF | (17)

Given the lengths of AD, AE, and DE, using the law of cosine:

∠ADH = arccos (L

2
AD + L

2
DE − L

2
AE
2LADLDE
) | (18)
∠AHD = ∠F DH = arctan(LEF , LDF ) | (19)
θ1 = 180◦ − ∠ADH − ∠AHD | (20)

Then, we can use θ1 to calculate the stroke length s.

Let α = α3 + α4:

α = 180◦ − θ1 − ϕ2 | (21)

xAR = cos(α)LAQ +

q
L

2
QR − (sin(α)LAQ − yAR)
2 | (22)
s = xARmax − xAR | (23)

### 3.3 Tool Tip Velocity

Calculating the tool tip velocity relative to frame {a} can also be quite challenging. If you attempt to take the time derivatives of eq.(12) and eq.(13), you’ll find the expressions of ˙θ1 and ˙θ2 are very messy because you need to take derivative of arctan and arccos functions, and the final expressions become unwieldy and difficult to interpret.
To address this, I use a technique known as the Instantaneous Center of Velocity method to make the expressions of ˙θ1 and ˙θ2 short and clear. If you’ve taken a course in mechanisms or dynamics, you may already be familiar with it. If not, the basic idea is that at any given instant, a rigid link in planar motion can be treated as rotating about a specific point in space, known as the instantaneous center. In our case, these points are labeled as I and J, as illustrated in Fig.(4).

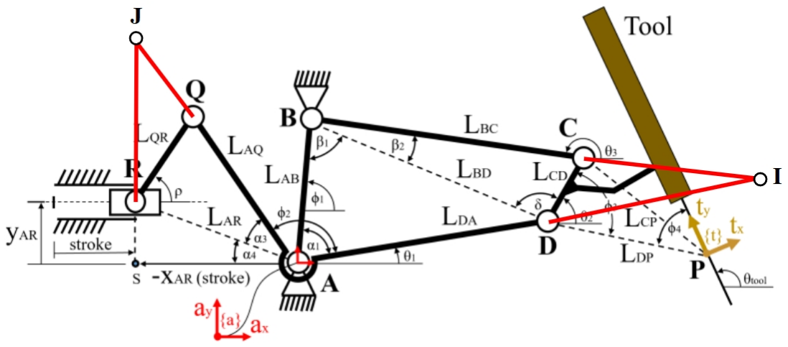
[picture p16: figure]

Figure 4: Velocity analysis for four-bar link and crank slider mechanism

For example, at any instant, link QR can be assumed to be in pure rotation with respect to the point J, where QJ is perpendicular to the velocity of point Q and RJ is perpendicular to the velocity of point R.

Then, we can get:

LJR = tan(α) · xAR − yAR | (24)
LJQ = sec(α) · xAR − LAQ | (25)

ρ˙ =

s˙

LJR

(26)

LAQ · α˙ = −LJQ · ρ˙ | (27)

˙θ1 = ˙α = −

LJQ

LAQ

ρ˙ | (28)

After determined ˙θ1, we want to find ˙θ2 and corresponding linear velocities P˙
x and P˙
y.

Similarly, link CD can be assumed to be in pure rotation with respect to the point I, where CI is perpendicular to the velocity of point C and DI is perpendicular to the velocity of point D.

β2 = arccos (L

2
BC + L

2
BD − L

2
CD
2LBCLBD
) | (29)

Let β = β1 + β2:

∠AIB = 180◦ − α1 − β | (30)

Then, apply the law of sine:

LAB sin(∠AIB)
=

LIA sin(β)
=
LIB sin(α1) | (31)

Since sin(180◦ − α1 − β) = sin(α1 + β):

LIA =

LAB · sin(β)
sin(α1 + β)

(32)

LID = LIA − LDA | (33)

Using Instantaneous Center method:

˙θ1LDA = − ˙θ2LID | (34)

˙θtool = ˙θ2 = −

LDA

LID

˙θ1 | (35)

From eq.(28) and eq.(26), we can get:

˙θtool =

LDALJQ

LIDLAQLJR

s˙ | (36)

Noted that LJQ(s), LID(s), and LJR(s) are not constants.

Thus eq.(36) has the form of: ˙θtool = f(s) ˙s

Then, taking derivative to eq.(12) and eq.(13), we can get the linear velocity of the tool tip:

P˙

x = − sin(θ1)LDA ˙θ1 − sin(θ2 − ϕ3)LDP ˙θ2 | (37)

P˙

y = cos(θ1)LDA ˙θ1 + cos(θ2 − ϕ3)LDP ˙θ2 | (38)

where
˙θ1 = −

LJQ

LAQLJR

s˙ | (39)

˙θ2 =

LDALJQ

LIDLAQLJR

s˙ | (40)

We now obtain a clear and compact expression for the velocity of point P.

## 4 Roll Mechanism


Figure 5: Kinematics diagram of the frames of SHER-3.0

The roll mechanism is relatively straightforward. As illustrated in Fig.(5), the roll angle ψ is defined with respect to the z-axis of frame {p}, and the rotational velocity ψ˙
is directly contolled
by the motor, with the positive direction defined along the x-axis of the base frame {b}. The roll axis is located d1 mm above the delta platform {p}, and frame {a} is positioned d3 mm above along the z-axis of frame {r}.

However, it is important to note that the orientations of frames {a} and {r} are different. In the home configuration, the vertical axis of frame {a} is y-axis, whereas the vertical axis of frame {r} is z-axis. Additional geometric details and frame assignments are shown in Fig.(6).

## 5 Tool Tip Velocity in Delta Platform Frame

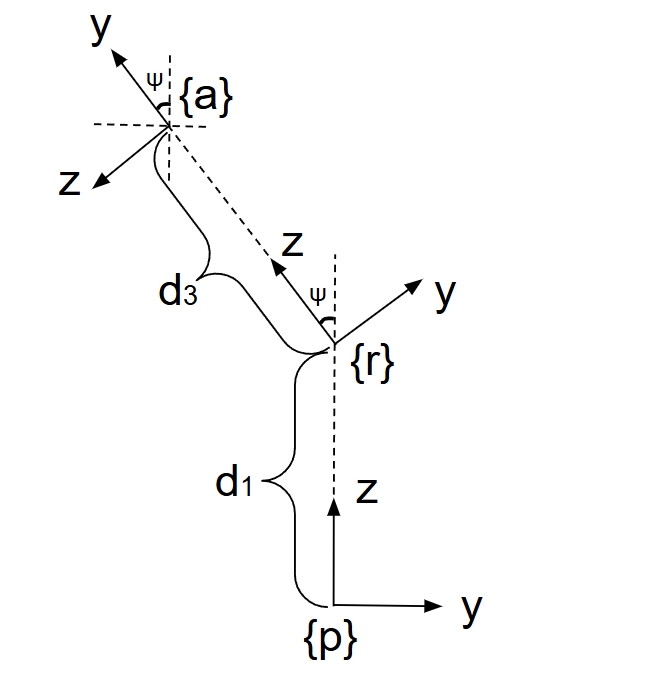
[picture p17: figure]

Figure 6: Front view of frames {p}, {r}, {a} of SHER-3.0

Recall that all previous kinematic derivations for the tool tip were expressed in frame {a}. To express the tool tip velocity in the delta platform frame {p}, we need to apply the following coordinate transformations:

First, define the homogeneous transformation matrix Tpr, which represents the transformation from frame frame {p} to frame {r}:

Tpr =

1 | 0 | 0 | 0
0 cos(ψ) − sin(ψ) 0
0 sin(ψ) | cos(ψ) | d1
0 | 0 | 0 | 1

(41)

Similarly, define the homogeneous transformation matrix Tra, which represents the transformation from frame {r} to frame {a}:

Tra =

1 | 0 | 0 | d2
0 cos(90◦
| | ) − sin(90◦
) 0
0 sin(90◦
) | cos(90◦
) | d3
0 | 0 | 0 | 1

(42)

Then, by multiplying the two matrices, we obtain the transformation matrix Tpa:

Tpa = TprTra =

1 | 0 | 0 | d2
0 − sin(ψ) − cos(ψ) | − sin(ψ)d3
0 | cos(ψ) | − sin(ψ) cos(ψ)d3 + d1
0 | 0 | 0 | 1

(43)

Given the tool tip position P expressed in frame {a} as P{a} , we can compute its coordinates in frame{p}, denoted as P{p} = TpaP{a}
:

Since the four-bar linkage is a planar mechanism, the z-component of the tool tip position in frame {a}, Pz{a}
is always zero.

Px{p}

Py{p}

Pz{p}
1

=

1 | 0 | 0 | d2
0 − sin(ψ) − cos(ψ) | − sin(ψ)d3
0 | cos(ψ) | − sin(ψ) cos(ψ)d3 + d1
0 | 0 | 0 | 1

Px{a}

Py{a}
0
1

(44)

Px{p}

Py{p}

Pz{p}

- =
| | Px{a} + d2
− sin(ψ)Py{a} − sin(ψ)d3
cos(ψ)Py{a} + cos(ψ)d3 + d1
- (45)

By taking the time derivative of eq.(45), we obtain the expression for the tool tip velocity in frame {p}:

P˙
x{p}
P˙
y{p}
P˙
z{p}
- =

P˙
x{a}
− sin(ψ)P˙

y{a} − cos(ψ)ψ˙(Py{a} + d3) cos(ψ)P˙

y{a} − sin(ψ)ψ˙(Py{a} + d3)

- (46)

For the angular velocity, the components can be easily identified:

˙θx{p}

˙θy{p}

˙θz{p}

- =

ψ˙
− cos(ψ)

˙θ2
− sin(ψ)

˙θ2

- (47)

where ψ˙

is the roll velocity and ˙θ2 is the tilt velocity.

Thus, we can express the tool tip velocity in frame {p} as:

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
x{a}
− sin(ψ)P˙

y{a} − cos(ψ)ψ˙(Py{a} + d3) cos(ψ)P˙

y{a} − sin(ψ)ψ˙(Py{a} + d3) ψ˙
− cos(ψ)

˙θ2
− sin(ψ)

˙θ2

(48)

where

P˙

x{a} = − sin(θ1)LDA ˙θ1 − sin(θ2 − ϕ3)LDP ˙θ2

P˙

y{a} = cos(θ1)LDA ˙θ1 + cos(θ2 − ϕ3)LDP ˙θ2

Py{a} = sin(θ1)LDA + sin(θ2 − ϕ3)LDP

˙θ2 =

LDALJQ

LIDLAQLJR

s˙

(49)

## 6 Kinematics Simulation and Visualization

The visualization script is available at https://github.com/zhaob5/roll_tilt_mechanism. This simple simulation only focuses on the four-bar linkage mechanism, with all coordinates defined in frame {a}. The tool tip velocity and trajectory are also visualized, currently limited to 2-D planar space. Feel free to follow the page for updates or contribute if you’re interested.

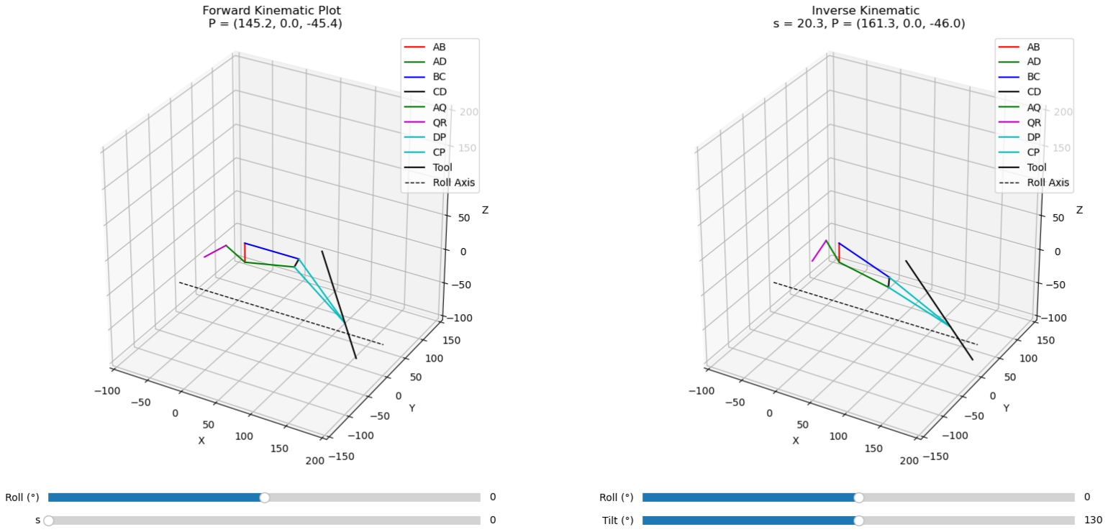
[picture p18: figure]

Figure 7: Forward Kinematics Visualization Figure 8: Inverse Kinematics Visualization

## 7 Disclaimer

The calculations and methods presented in this document are based on my personal understanding and interpretation of the roll and tilt mechanism of SHER-3.0. I hope the derivations provide useful insights and inspiration for your own work. Please note that if you define coordinate frames or the home configuration differently than described here, your results may differ. Therefore, it is more important to understand the principles of the derivation than to directly copy the final expressions into your work. While I’ve made every effort to ensure accuracy, there may still be errors or oversights. I strongly encourage you to verify the results independently before applying them in any critical context. If you have suggestions, corrections, or would like to discuss the topic further, feel free to reach out to me at: bzhao17@alumni.jh.edu.

## 8 Appendix: Python Scripts

### 8.1 Forward Kinematics Visualization

1 | # -*- coding: utf-8 -*-
2 | """
3 | SHER-3.0 Tilt-Roll Forward Kinematics Visualization

4
5 Created on Thu Jun 19 13:26:00 2025

6
7 | @author: Botao Zhao
8 | """

9
10 | import numpy as np
11 | import matplotlib.pyplot as plt
12 | from matplotlib.widgets import Slider

13
14 | def ROTz(theta):
15 | return np.array([[np.cos(theta), -np.sin(theta), 0],
16 | [np.sin(theta), | np.cos(theta), 0],
17 | [0, | 0, | 1]])

18
19 | def Pos(theta, L):
20 | return np.array([[L*np.cos(theta)],
21 | [L*np.sin(theta)],
22 | [0]])

23
24 | def Trans(R, p):
25 | T = np.vstack((np.hstack((R, p)), [0, 0, 0, 1]))
26 | return T

27
28 | def apply_roll_rotation(points, angle_deg, offset_z):
29 | angle_rad = np.deg2rad(angle_deg)
30 | R = np.array([[1, 0, 0],
31 | [0, np.cos(angle_rad), -np.sin(angle_rad)],
32 | [0, np.sin(angle_rad), | np.cos(angle_rad)]])
33 | rotated = []
34 | for p in points:
35 | p_shifted = p - np.array([0, 0, offset_z])
36 | p_rotated = R @ p_shifted + np.array([0, 0, offset_z])
37 | rotated.append(p_rotated)
38 | return rotated

39
40 | # Fixed Parameters
41 | x_AR_l = -60.48
42 | y_AR = -10
43 | L_AQ = 32.5
44 | L_QR = 42
45 | L_AB = 28
46 | L_BC = 78.5
47 | L_CD = 15
48 | L_DA = 73.5
49 | phi1 = np.pi / 2
50 | phi2 = np.pi * 138 / 180

L_DP = 94.49
phi3 = np.pi * 103.93 / 180
phi4 = np.pi * 31.06 / 180
L_T = 50
d1 = -25.5 # Distance between the center frame of the delta platform to point A

# Create figure and axes

fig = plt.figure(figsize=(10, 8))
ax = fig.add_subplot(111, projection='3d') fig.subplots_adjust(bottom=0.15)

# Slider axes

slider_ax_s = fig.add_axes([0.2, 0.02, 0.6, 0.03]) slider_ax_roll = fig.add_axes([0.2, 0.06, 0.6, 0.03])

# Create sliders

s_slider = Slider(slider_ax_s, 's', 0, 50, valinit=0)
roll_slider = Slider(slider_ax_roll, 'Roll (°)', -90, 90, valinit=0)

def update_plot(_=None):
s = s_slider.val
roll = roll_slider.val
ax.cla()

x_AR = x_AR_l + s
L_AR = np.sqrt(x_AR**2 + y_AR**2)
alpha3 = np.arccos((L_AR**2 + L_AQ**2 - L_QR**2) / (2 * L_AR * L_AQ)) alpha4 = np.pi - np.arctan2(y_AR, x_AR)

theta1 = np.pi - (phi2 + alpha3 + alpha4)
alpha1 = phi1 - theta1
L_BD = np.sqrt(L_AB**2 + L_DA**2 - 2 * L_AB * L_DA * np.cos(alpha1)) beta1 = np.arccos((L_AB**2 + L_BD**2 - L_DA**2) / (2 * L_AB * L_BD))

delta = np.arccos((L_CD**2 + L_BD**2 - L_BC**2) / (2 * L_CD * L_BD)) theta2 = phi1 + beta1 - delta

T_AD = Trans(ROTz(theta1), Pos(theta1, L_DA))
T_DP = Trans(ROTz(theta2 - phi3 - theta1), Pos(theta2 - phi3 - theta1, L_DP))
T_PT = Trans(ROTz(np.pi / 2 - phi4 - (theta2 - phi3 - theta1)), Pos(np.pi / 2 - phi4 - (theta2 - phi3 - theta1), 0)) T_AT = T_AD @ T_DP @ T_PT

thetat = -np.arccos(T_AT[0][0])
pt = np.array([T_AT[0][3], 0, T_AT[1][3]])
p_tip = pt + np.array([np.cos(thetat)*L_T, 0, np.sin(thetat)*L_T]) p_end = pt + np.array([-np.cos(thetat)*L_T*2, 0, -np.sin(thetat)*L_T*2])

# Define original points

A = np.array([0, 0, 0])
B = A + np.array([0, 0, L_AB])
D = A + np.array([np.cos(theta1) * L_DA, 0, np.sin(theta1) * L_DA])
C = D + np.array([np.cos(theta2) * L_CD, 0, np.sin(theta2) * L_CD])
Q = A + np.array([-np.cos(alpha3 + alpha4) * L_AQ, 0, np.sin(alpha3 + alpha4) * L_AQ]) R = np.array([x_AR, 0, y_AR])

P = D + np.array([np.cos(phi3 - theta2) * L_DP, 0, -np.sin(phi3 - theta2) * L_DP])

# Apply roll rotation to all points

raw_points = [A, B, C, D, Q, R, P, p_tip, p_end]
A, B, C, D, Q, R, P, p_tip, p_end = apply_roll_rotation(raw_points, roll, d1)

# Plot links

ax.plot([A[0], B[0]], [A[1], B[1]], [A[2], B[2]], 'r', label='AB') ax.plot([A[0], D[0]], [A[1], D[1]], [A[2], D[2]], 'g', label='AD') ax.plot([B[0], C[0]], [B[1], C[1]], [B[2], C[2]], 'b', label='BC') ax.plot([C[0], D[0]], [C[1], D[1]], [C[2], D[2]], 'k', label='CD') ax.plot([A[0], Q[0]], [A[1], Q[1]], [A[2], Q[2]], 'g', label='AQ') ax.plot([Q[0], R[0]], [Q[1], R[1]], [Q[2], R[2]], 'm', label='QR')
ax.plot([D[0], P[0]], [D[1], P[1]], [D[2], P[2]], 'c', label='DP')
ax.plot([C[0], P[0]], [C[1], P[1]], [C[2], P[2]], 'c', label='CP')
ax.plot([p_tip[0], p_end[0]], [p_tip[1], p_end[1]], [p_tip[2], p_end[2]], 'k', label='Tool')

# Plot the roll axis (dashed black line)

x_range = np.array([-100, 200])
y_fixed = np.array([0, 0])
z_fixed = np.array([-60, -60])
ax.plot(x_range, y_fixed, z_fixed, 'k--', linewidth=1, label='Roll Axis')

# Axis settings

ax.set_xlim([-100, 200])
ax.set_ylim([-150, 150])
ax.set_zlim([-100, 200])
ax.set_box_aspect([1, 1, 1]) ax.set_xlabel("X")
ax.set_ylabel("Y")
ax.set_zlabel("Z")
ax.set_title(f"Forward Kinematic Plot \n P = ({P[0]:.1f}, {P[1]:.1f}, {P[2]:.1f})") ax.legend()

# Initial draw

update_plot()

# Connect sliders

s_slider.on_changed(update_plot) roll_slider.on_changed(update_plot)

plt.show()

### 8.2 Inverse Kinematics Visualization

# -*- coding: utf-8 -*-

"""
SHER-3.0 Tilt-Roll Inverse Kinematics Visualization

Created on Thu Jun 19 11:27:24 2025

@author: Botao Zhao
"""
import numpy as np
import matplotlib.pyplot as plt
from matplotlib.widgets import Slider

# offset_z is the distance between the center frame of the delta platform to point A on the tilt mechanism def apply_roll_rotation(points, angle_deg, offset_z):

angle_rad = np.deg2rad(angle_deg)
R = np.array([[1, 0, 0],
[0, np.cos(angle_rad), -np.sin(angle_rad)],
18 | [0, np.sin(angle_rad), | np.cos(angle_rad)]])
rotated = []
| for p in points:
p_shifted = p - np.array([0, 0, offset_z])
p_rotated = R @ p_shifted + np.array([0, 0, offset_z])
| rotated.append(p_rotated) return rotated

# Constants

AB = 28
BC = 78.5
CD = 15
DA = 73.5
DP = 94.49
AQ = 32.5
QR = 42
x_AR_l = -60.48
y_AR = -10
L_T = 50
d1 = -25.5 # Distance between the center frame of the delta platform to point A
| # Angles in radians
phi1 = np.pi / 2
| phi2 = np.pi * 138 / 180 phi3 = np.pi * 103.93 / 180 phi4 = np.pi * 31.06 / 180

#print("theta2 = ", float(theta2*180/np.pi))

| theat_tool_max = 150 # deg theat_tool_min = 110 # deg theat_tool_init = 130 # deg
| # Create figure and axes fig = plt.figure(figsize=(10, 8))

ax = fig.add_subplot(111, projection='3d') fig.subplots_adjust(bottom=0.15)

# Slider axes

slider_ax_theta_tool = fig.add_axes([0.2, 0.02, 0.6, 0.03]) slider_ax_roll = fig.add_axes([0.2, 0.06, 0.6, 0.03])

# Create sliders

theta_tool_slider = Slider(slider_ax_theta_tool, 'Tilt (°)', theat_tool_min, theat_tool_max, valinit=theat_tool_init) roll_slider = Slider(slider_ax_roll, 'Roll (°)', -90, 90, valinit=0)

def update_plot(_=None):
theta_tool = theta_tool_slider.val * np.pi/180
roll = roll_slider.val
ax.cla()

theta2 = phi3 - np.pi + phi4 + theta_tool a = CD*np.cos(theta2) - AB*np.cos(phi1)
b = - CD*np.sin(theta2) + AB*np.sin(phi1)
gamma = np.arctan2(a, b)
angle_adc = np.arccos((DA**2+a**2+b**2-BC**2)/(2*DA*np.sqrt(a**2+b**2))) theta1 = np.pi/2 - angle_adc + gamma

Px = np.cos(theta1)*DA + np.cos(phi3 - theta2)*DP
Py = np.sin(theta1)*DA - np.sin(phi3 - theta2)*DP

# Now find the slide bar position s:

alpha = np.pi - theta1 - phi2 # alpha = alpha3 + alpha4

x_AR = -np.cos(alpha)*AQ - np.sqrt(QR**2 - (np.sin(alpha)*AQ - y_AR)**2)

s = x_AR - x_AR_l

# Define points

A = np.array([0, 0, 0])
B = A + np.array([0, 0, AB])
D = A + np.array([np.cos(theta1) * DA, 0, np.sin(theta1) * DA]) C = D + np.array([np.cos(theta2) * CD, 0, np.sin(theta2) * CD]) Q = A + np.array([-np.cos(alpha) * AQ, 0, np.sin(alpha) * AQ]) R = np.array([x_AR, 0, y_AR])
P = np.array([Px, 0, Py])

# Tool shaft

p_tip = P + np.array([np.cos(theta_tool)*L_T*2, 0, np.sin(theta_tool)*L_T*2]) p_end = P + np.array([-np.cos(theta_tool)*L_T, 0, -np.sin(theta_tool)*L_T])

# Apply roll rotation to all points

raw_points = [A, B, C, D, Q, R, P, p_tip, p_end]
A, B, C, D, Q, R, P, p_tip, p_end = apply_roll_rotation(raw_points, roll, d1)

# Plot links

ax.plot([A[0], B[0]], [A[1], B[1]], [A[2], B[2]], 'r', label='AB') ax.plot([A[0], D[0]], [A[1], D[1]], [A[2], D[2]], 'g', label='AD') ax.plot([B[0], C[0]], [B[1], C[1]], [B[2], C[2]], 'b', label='BC')

107 | ax.plot([C[0], D[0]], [C[1], D[1]], [C[2], D[2]], 'k', label='CD')
108 | ax.plot([A[0], Q[0]], [A[1], Q[1]], [A[2], Q[2]], 'g', label='AQ')
109 | ax.plot([Q[0], R[0]], [Q[1], R[1]], [Q[2], R[2]], 'm', label='QR')
110 | ax.plot([D[0], P[0]], [D[1], P[1]], [D[2], P[2]], 'c', label='DP')
111 | ax.plot([C[0], P[0]], [C[1], P[1]], [C[2], P[2]], 'c', label='CP')
112 | ax.plot([p_tip[0], p_end[0]], [p_tip[1], p_end[1]], [p_tip[2], p_end[2]], 'k', label='Tool')

113
114 | # Plot the roll axis (dashed black line)
115 | x_range = np.array([-100, 200])
116 | y_fixed = np.array([0, 0])
117 | z_fixed = np.array([-60, -60])
118 | ax.plot(x_range, y_fixed, z_fixed, 'k--', linewidth=1, label='Roll Axis')

119
120 | # Axis settings
121 | ax.set_xlim([-100, 200])
122 | ax.set_ylim([-150, 150])
123 | ax.set_zlim([-100, 200])
124 | ax.set_box_aspect([1, 1, 1])
125 | ax.set_xlabel("X")
126 | ax.set_ylabel("Y")
127 | ax.set_zlabel("Z")
128 | ax.set_title(f"Inverse Kinematic \n s = {s:.1f}, P = ({P[0]:.1f}, {P[1]:.1f}, {P[2]:.1f})")
129 | ax.legend()

130
131 | # Initial draw
132 | update_plot()

133
134 | # Connect sliders
135 | theta_tool_slider.on_changed(update_plot)
136 | roll_slider.on_changed(update_plot)

137
138 plt.show()

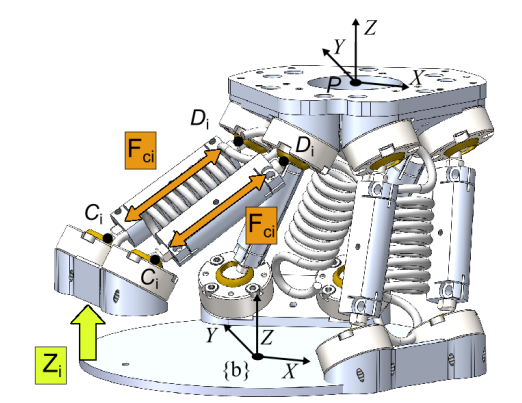
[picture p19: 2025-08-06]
Figures/Delta_Platform.png

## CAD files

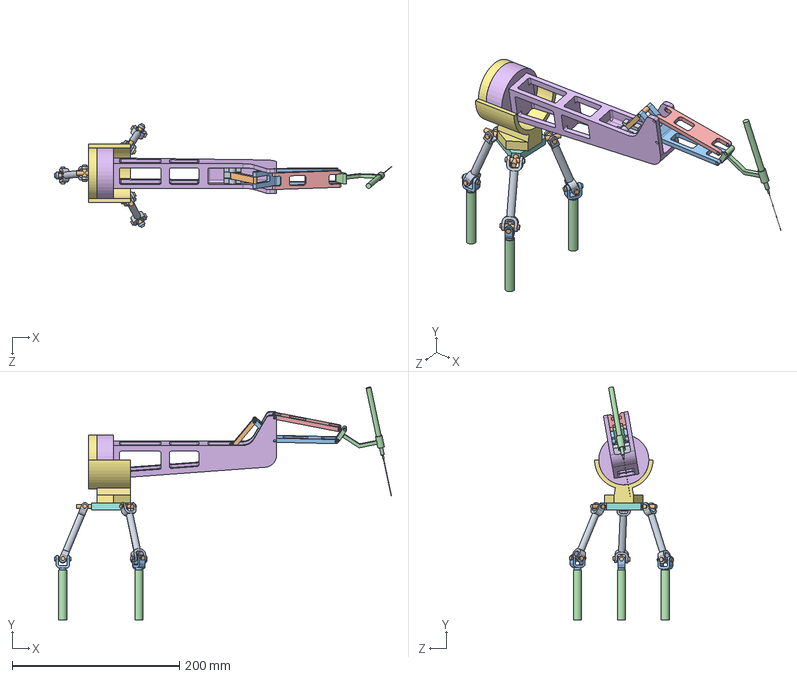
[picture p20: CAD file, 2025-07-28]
CAD Model/SHER-3.0.SLDASM
403.2 x 278.7 x 124.9 mm
base_link x 3
prismatic_joint x 3
universal_joint x 6
link_l x 3
platform
roll_housing
four_bar_ab
four_bar_bc
four_bar_cd
four_bar_da
four_bar_qr
slider

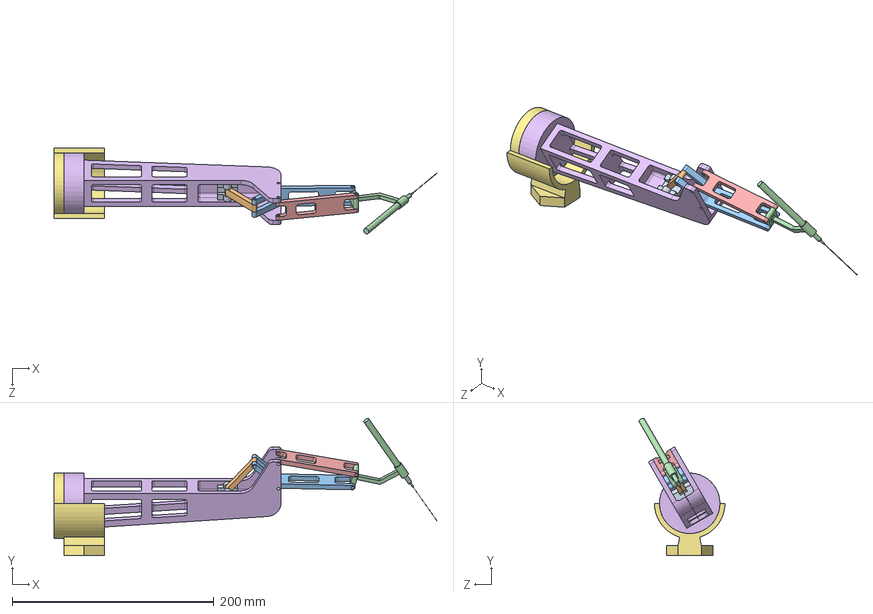
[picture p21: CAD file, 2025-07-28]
CAD Model/roll_tilt_mechanism.SLDASM
380.0 x 136.4 x 85.3 mm
roll_housing
four_bar_ab
four_bar_bc
four_bar_cd
four_bar_da
four_bar_qr
slider

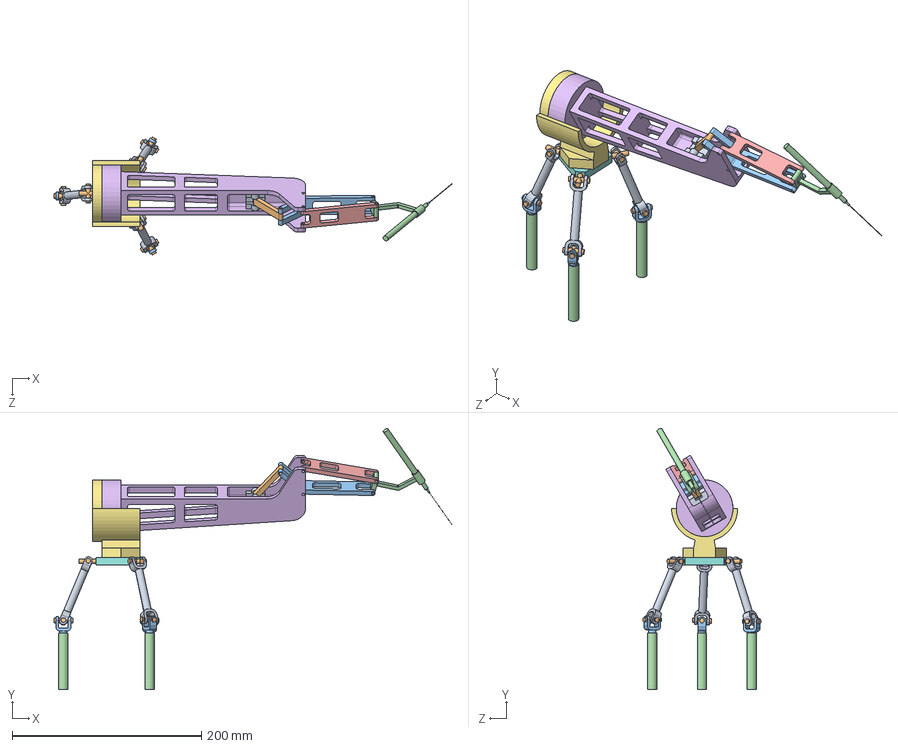
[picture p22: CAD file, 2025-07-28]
CAD Model/delta_platform.SLDASM
420.7 x 276.1 x 124.9 mm
base_link x 3
prismatic_joint x 3
universal_joint x 6
link_l x 3
platform
roll_housing
four_bar_ab
four_bar_bc
four_bar_cd
four_bar_da
four_bar_qr
slider

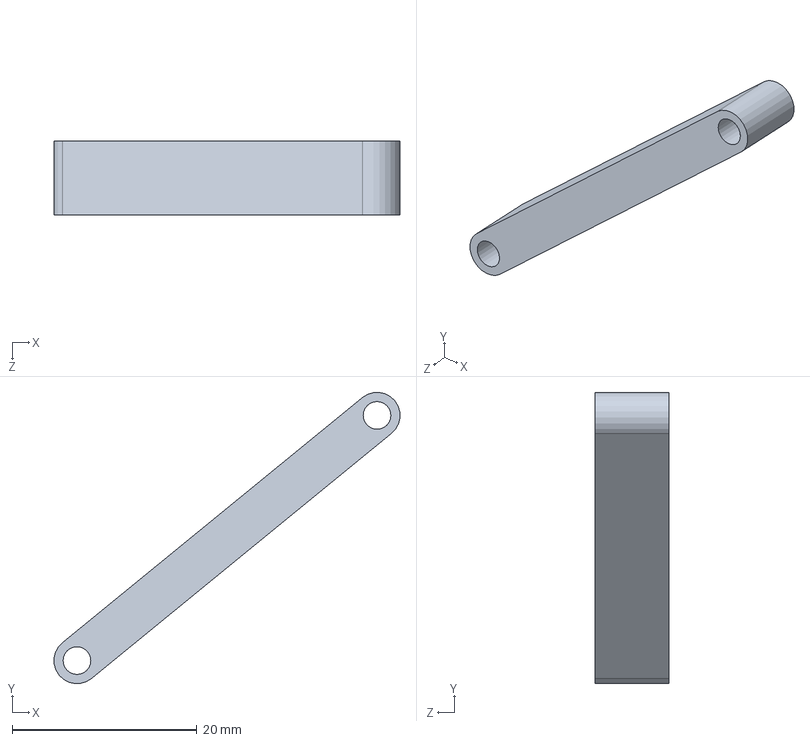
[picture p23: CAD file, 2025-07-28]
CAD Model/four_bar_qr.SLDPRT
37.5 x 31.5 x 8.00 mm

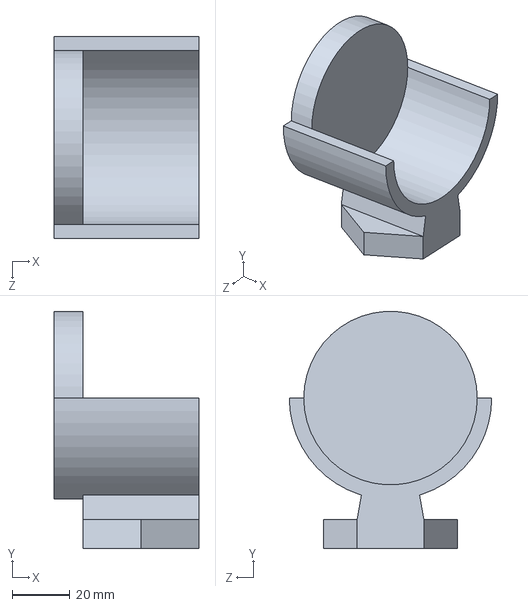
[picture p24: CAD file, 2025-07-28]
CAD Model/roll_housing.SLDPRT
50.0 x 81.9 x 70.0 mm

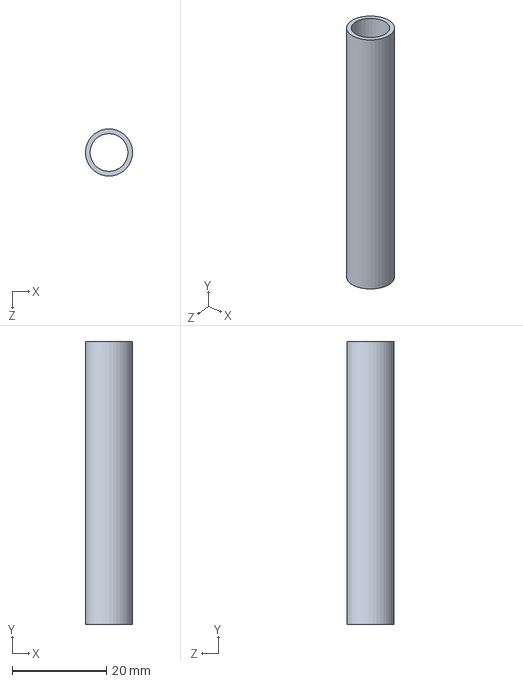
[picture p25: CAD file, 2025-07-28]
CAD Model/base_link.SLDPRT
9.97 x 60.0 x 10.0 mm

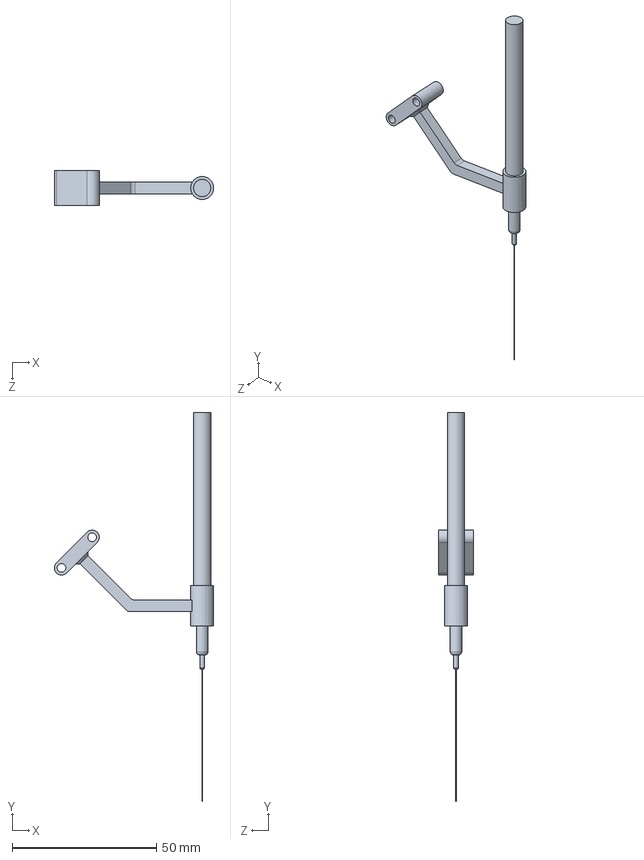
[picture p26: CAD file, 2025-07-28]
CAD Model/four_bar_cd.SLDPRT
55.3 x 134.8 x 12.0 mm

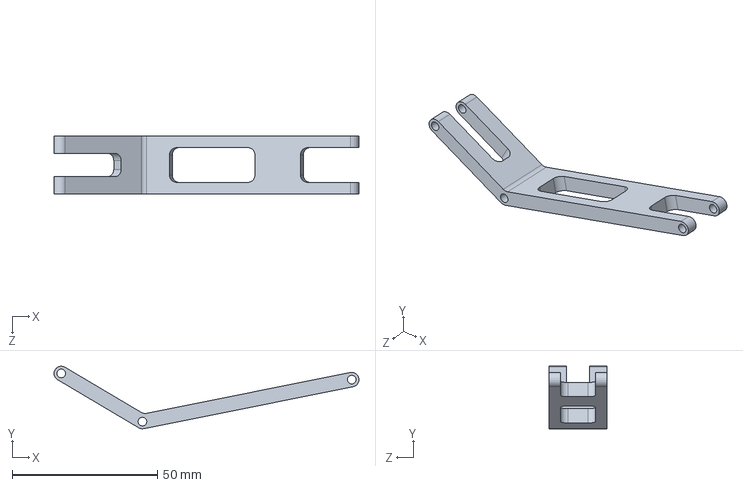
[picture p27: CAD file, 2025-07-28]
CAD Model/four_bar_da.SLDPRT
105.0 x 21.6 x 20.0 mm

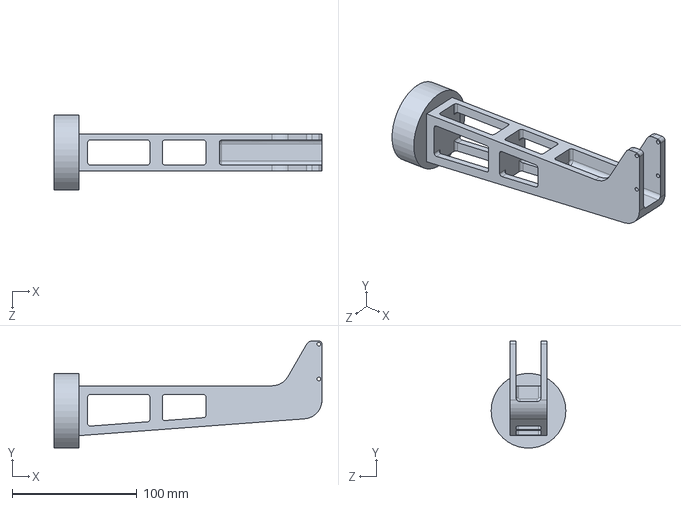
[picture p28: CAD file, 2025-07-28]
CAD Model/four_bar_ab.SLDPRT
215.2 x 85.9 x 60.0 mm

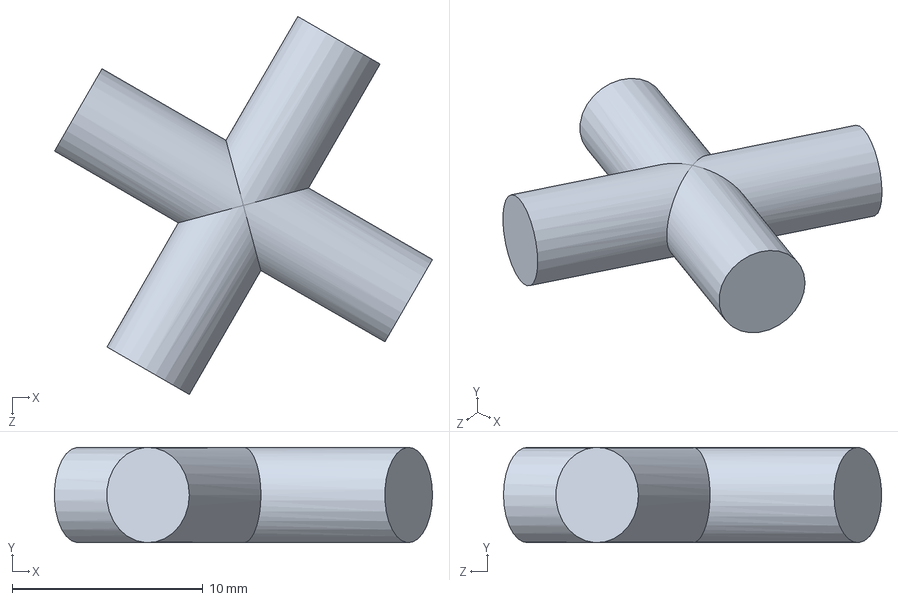
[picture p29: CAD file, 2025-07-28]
CAD Model/universal_joint.SLDPRT
19.8 x 5.00 x 19.8 mm

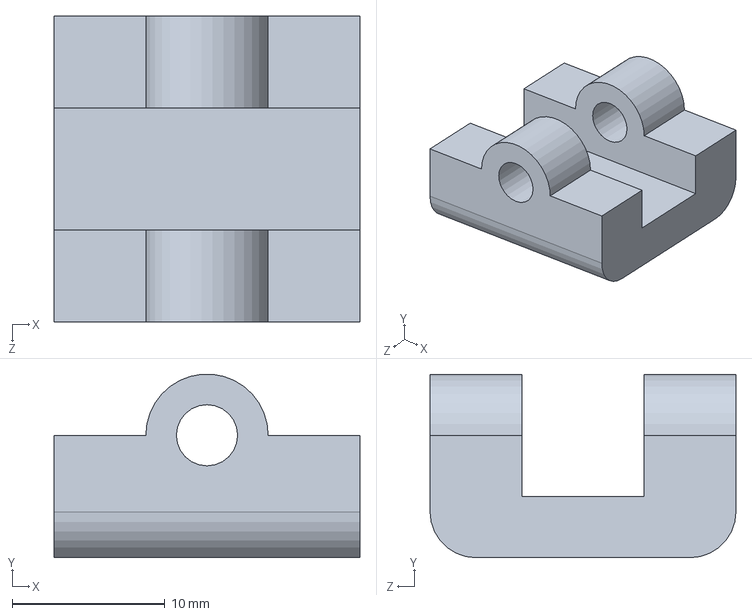
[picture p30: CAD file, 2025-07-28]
CAD Model/slider.SLDPRT
20.0 x 12.0 x 20.0 mm

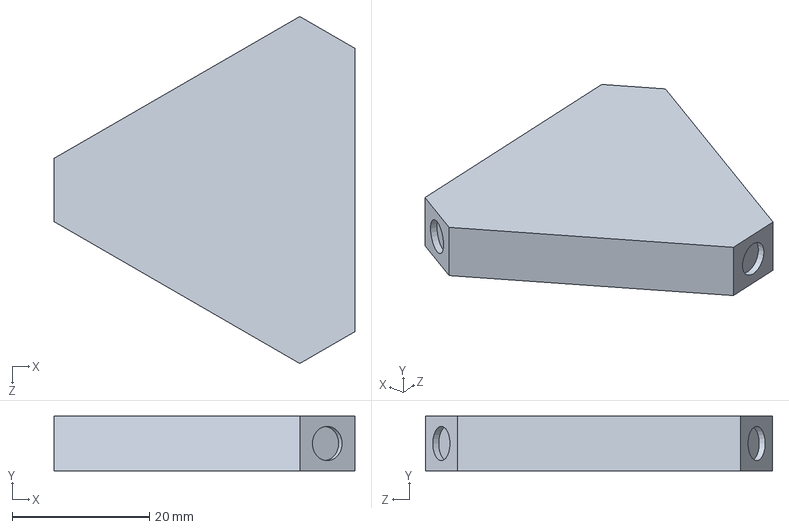
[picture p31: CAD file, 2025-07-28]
CAD Model/platform.SLDPRT
43.7 x 8.00 x 50.5 mm

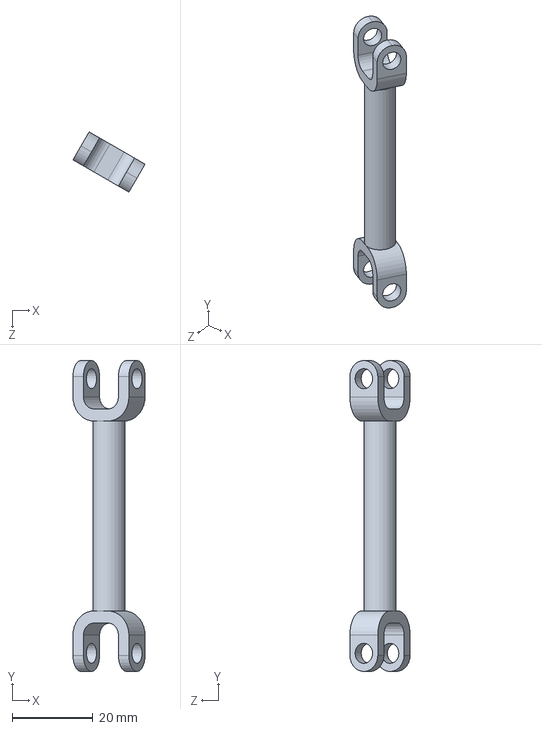
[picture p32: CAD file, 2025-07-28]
CAD Model/link_l.SLDPRT
17.9 x 77.0 x 14.9 mm

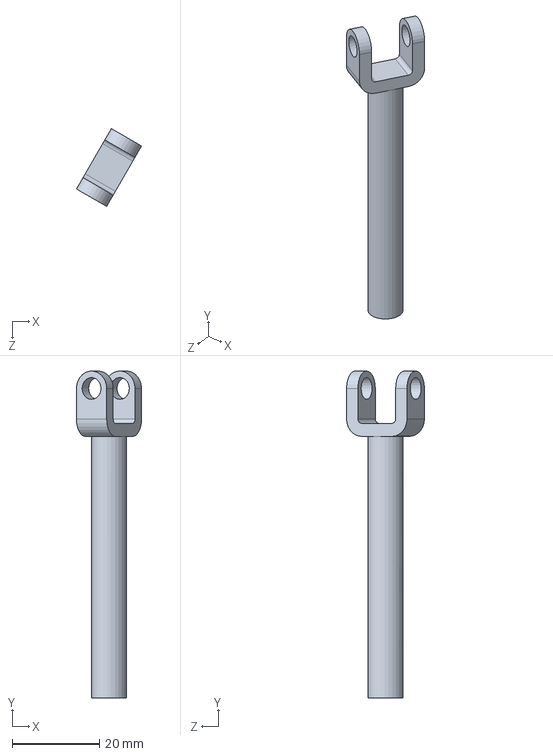
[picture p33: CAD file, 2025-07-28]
CAD Model/prismatic_joint.SLDPRT
14.9 x 75.0 x 17.9 mm

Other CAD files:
CAD Model/Motion_Analysis.SLDASM
CAD Model/four_bar_bc.SLDPRT

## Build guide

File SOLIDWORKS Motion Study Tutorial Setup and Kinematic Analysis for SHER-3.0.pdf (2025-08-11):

## SOLIDWORKS Motion Study Tutorial: Setup and Kinematic Analysis for SHER-3.0

Botao Zhao

August 11, 2025

## Contents

1 Introduction | 2
2 Setting Up and Running a Motion Study | 3
3 Result Analysis | 6
4 Disclaimer | 7

## 1 Introduction

This guide is intended for readers who are new to SOLIDWORKS Motion Study and want a practical starting point for applying it to robotic system design. From my perspective, Motion Study is an extremely convenient tool for quickly validating a robot’s design, performing preliminary kinematic checks, and gaining early insights into structural analysis without needing a full simulation package. Its workflow supports rapid iteration, allowing you to modify your design and immediately observe the effects on motion and performance.

Using the SHER-3.0 robot arm as an example, this tutorial walks through the setup and execution of a kinematic analysis, helping you understand how to use Motion Study effectively for early-stage design validation. The CAD files and kinematic equations of SHER-3.0 are available at: https://github.com/zhaob5/sher3-kinematics

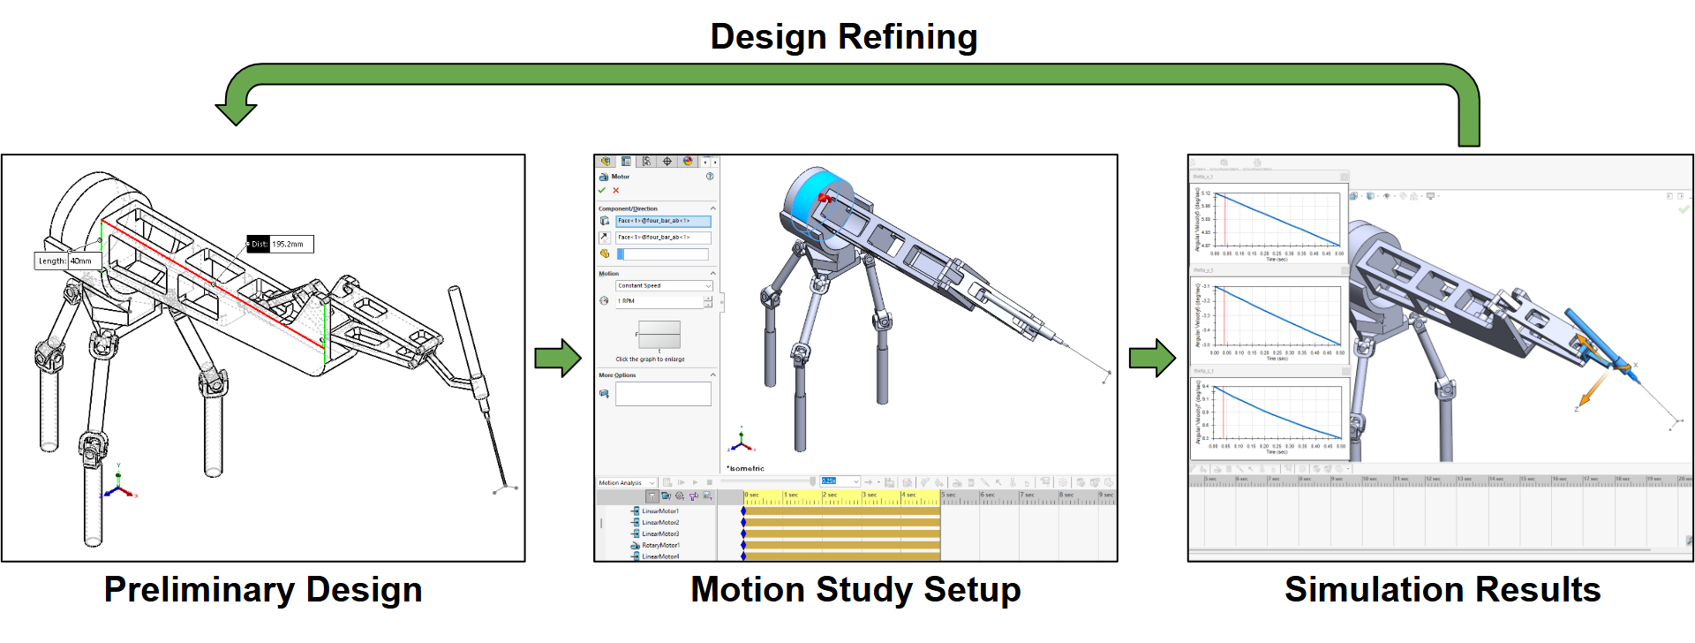
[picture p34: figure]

Figure 1: SolidWorks Motion Study Workflow

## 2 Setting Up and Running a Motion Study

To create a Motion Study, enable SOLIDWORKS Motion in Tools > Add-ins.

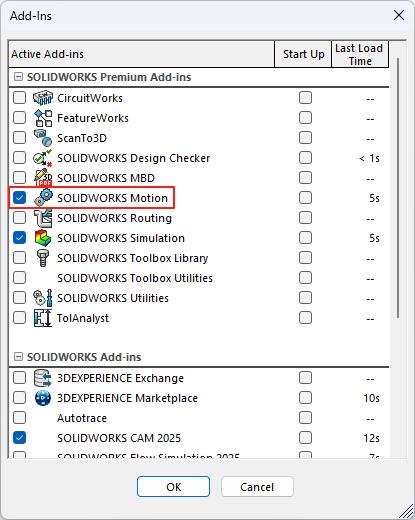
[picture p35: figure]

Figure 2: SOLIDWORKS Add-Ins Dialog

### 2.1 Prepare the Home Configuration

Begin by positioning your robot assembly in its home or zero configuration. This will serve as the starting point for your motion analysis. Ensure all mates and constraints are correctly defined so that the mechanism moves as intended.

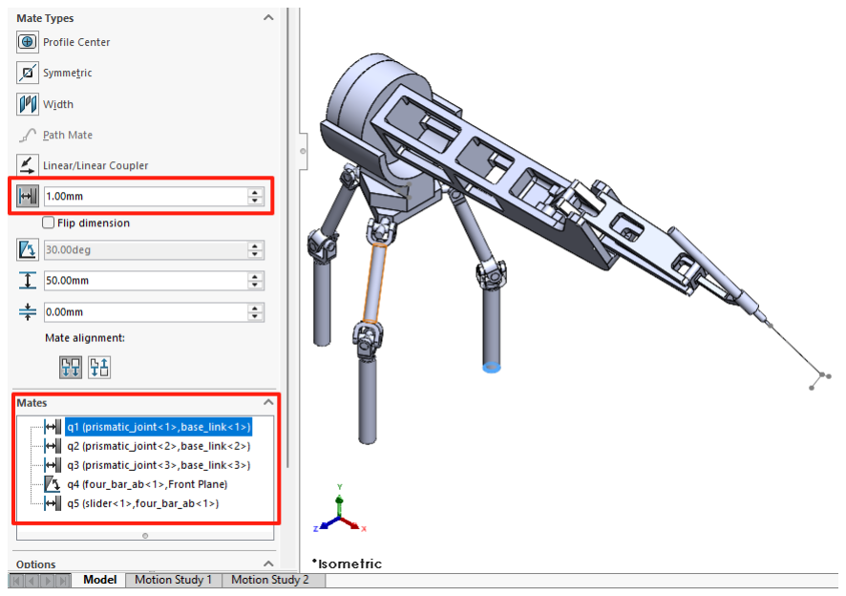
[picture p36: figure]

Figure 3: Home Configuration Setup in Assembly Model

### 2.2 Switch to Motion Study Mode

In the assembly environment, click Motion Study tab, then open the dropdown menu at the lower left of the screen and select Motion Analysis. This will bring up the Motion Study timeline and toolset, where you can define motion inputs, simulation parameters, and analysis outputs.

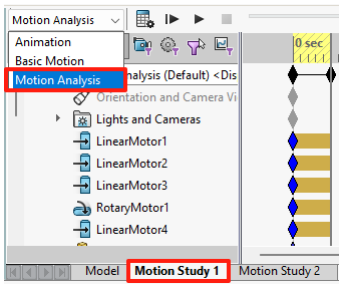
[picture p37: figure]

Figure 4: Select Motion Analysis Mode

### 2.3 Assign Motors and Motion Inputs

For each joint or actuator, assign the appropriate motor type (rotary or linear) and specify the desired speed. SOLIDWORKS allows you to control motion either with constant values or with functions over time, enabling more realistic simulation of joint trajectories.

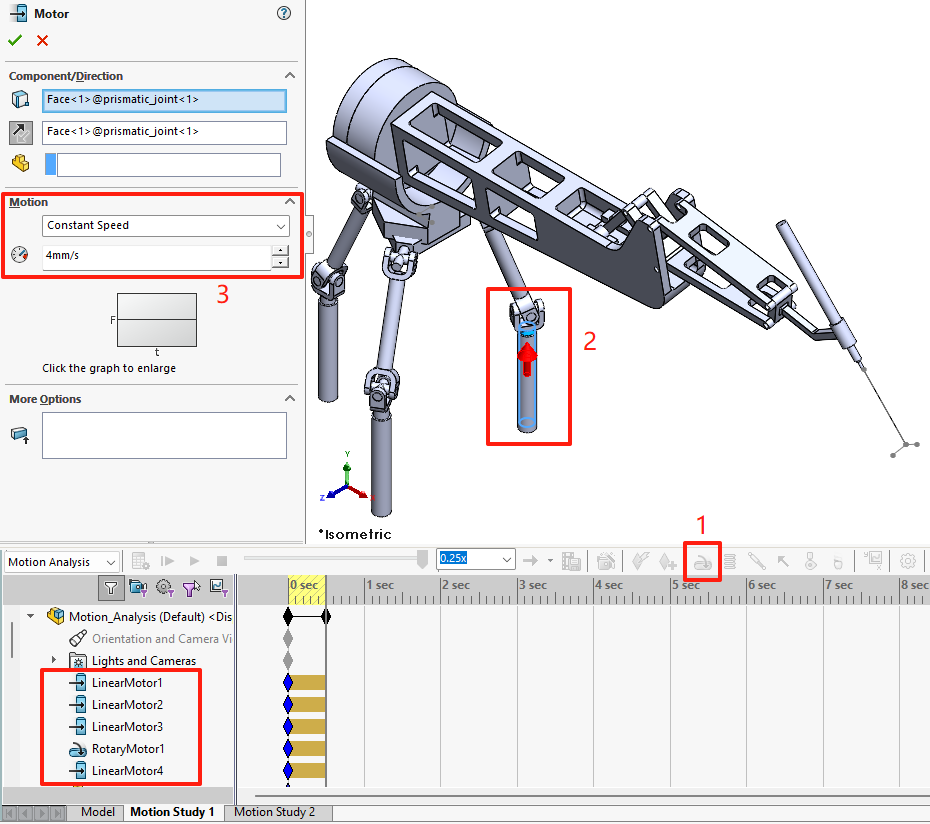
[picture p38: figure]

Figure 5: Motor Setup

### 2.4 Set the Simulation Time

Define the total duration of the motion study in the timeline settings. Adjusting this parameter controls how long the simulation runs and determines the resolution of your results.

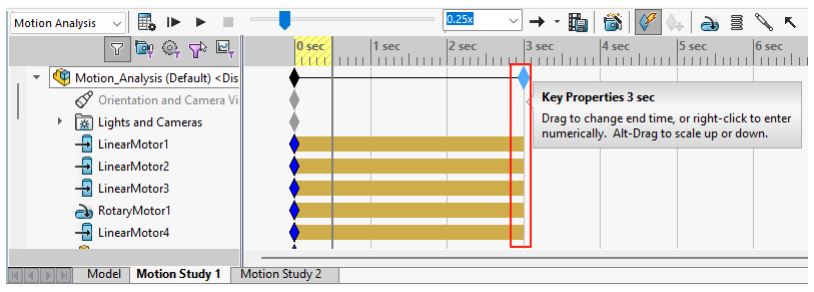
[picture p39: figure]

Figure 6: Simulation Time Setup

### 2.5 Run the Simulation

Once the setup is complete, run the simulation. Once the setup is complete, run the simulation. After it finishes, click the Results and Plots icon to generate motion data. To plot linear velocity, select a specific point on the part. To plot angular velocity, select a surface or feature that represents the rotating body. This ensures that SOLIDWORKS calculates the velocity data for the exact location or rotation you intend to analyze.

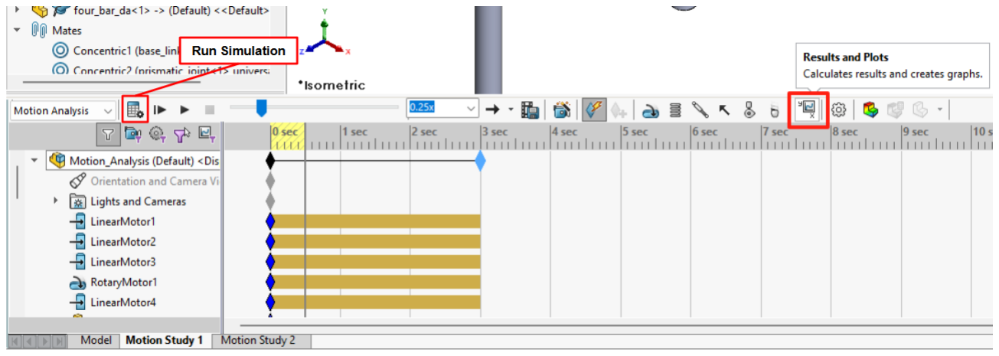
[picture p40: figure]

Figure 7: Run Simulation, Results and Plots Icons

## 3 Result Analysis

When choosing a reference frame, you may use the global frame defined in the assembly or a local reference frame created in the part file. Using a local frame is particularly useful for analyzing motion relative to a specific link in the robot arm.

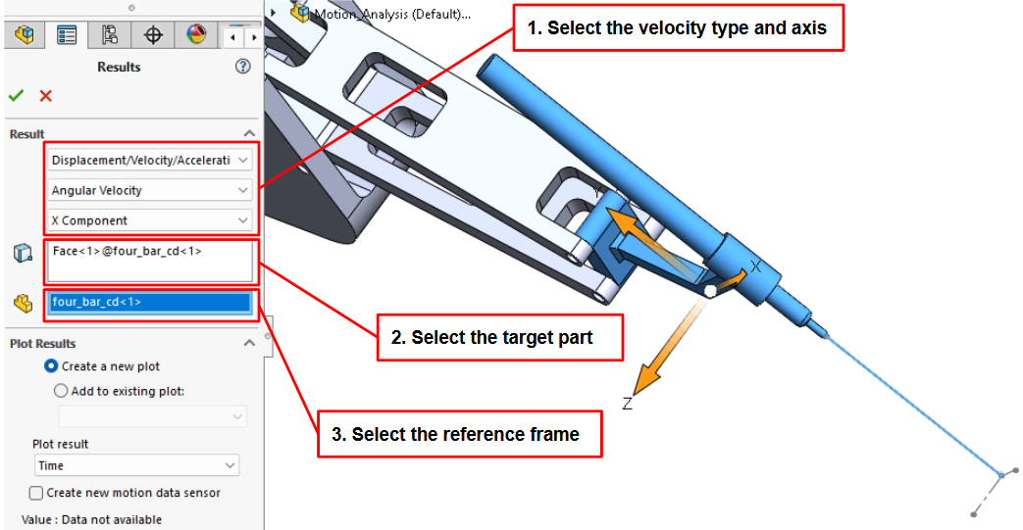
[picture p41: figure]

Figure 8: Result and Plot Setup Page

Since SOLIDWORKS Motion Study does not provide instantaneous velocity outputs directly at a specific configuration, you can use one of two approaches. First, you can export the simulation results to a .csv or similar spreadsheet file, then extract the velocity values corresponding to your desired time step. Alternatively, you can set the simulation’s time to the desired instant (e.g., t =
0) and read the velocity values directly from the results plot at that moment.


Figure 9: Linear and Angular Velocity Plots of SHER-3.0

## 4 Disclaimer

This guide is intended as a quick-start reference for setting up and running basic kinematic analyses in SOLIDWORKS Motion Study, using SHER-3.0 as an example. It is not a comprehensive training resource. If you are unfamiliar with SOLIDWORKS Motion Study or lack prior simulation experience, it is strongly recommended that you consult more detailed tutorials, official documentation, or formal training materials. The steps and examples provided here are based on my personal workflow and understanding, and may involve simplifications or assumptions that are not universally applicable. Readers should independently verify any results before applying them to critical design decisions or safety-related applications. If you spot any errors, have suggestions, or would like to discuss the topic further, feel free to reach out to me at: bzhao17@alumni.jh.edu.
